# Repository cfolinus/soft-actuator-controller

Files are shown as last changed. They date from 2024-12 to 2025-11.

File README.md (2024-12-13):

# soft-actuator-controller
The Trajectory Cycle program serves as a means of running a cyclic actuator inflation test. 
This program is designed for the arduino nano platform and is intended to be used with a
2/2 NC solenoid valves arranged in a fill/bleed circuit. The program is designed to be used with any soft pneumatic actuator, and requires tuning of PID gain values for different actuators. Zeigler-Nichols method is a recommended starting point.

The codebase will not be able to properly upload to the controller unless it is correctly formatted for your computer. Be sure to follow the PlatformIO and codebase installation instructions found in the "Install, Tune, & Run the Controller" How-to guide.

In the codebase, the main control loop can be found in main.cpp, but all variables relevant to the adjustment of the controller can be found in adjustableSettings.cpp. For details on how the controller works, what purpose it serves, what all relevant variables do, and how to tune the controller, please refer to the Powerpoint presentation and word documents included in this directory.

--Evan Comiskey, 2024/08, MIT Fabrication-Integrated Design Lab, comiskey@mit.edu

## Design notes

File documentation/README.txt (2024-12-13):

The Trajectory Cycle program serves as a means of running a cyclic actuator inflation test. 
This program is designed for the arduino nano platform and is intended to be used with a
2-way proportional solenoid valves arranged in a fill/bleed circuit. The program is designed to be used with any soft pneumatic actuator, and requires tuning of PID gain values for different actuators. Zeigler-Nichols method is a recommended starting point.

The codebase will not be able to properly upload to the controller unless it is correctly formatted for your computer. Be sure to follow the PlatformIO and codebase installation instructions found in the "Install, Tune, & Run the Controller" How-to Word document in the documentation sub-folder before downloading the entire GitHub repository.

In the codebase, the main control loop can be found in main.cpp, but all variables relevant to the adjustment of the controller can be found in adjustableSettings.cpp. For details on how the controller works, what purpose it serves, what all relevant variables do, and how to tune the controller, please refer to the Powerpoint presentation and word documents included in the documentation directory.

--Evan Comiskey, 2024/12, MIT Fabrication-Integrated Design Lab, comiskey@mit.edu

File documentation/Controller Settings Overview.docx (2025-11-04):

# Pneumatic Actuator Test Stand

# Controller Settings Overview

Evan Comiskey – MIT FID Lab – 2024/08 – comiskey@mit.edu

# Description:

This guide walks you through the functions of all variables relevant to the operation and adjustment of the test stand’s PID control software, in the order in which they appear in the main settings file. Any implied or uncontextualized purposes of variables discussed in this overview can likely be explained by reviewing the Test Stand & Controller Overview PowerPoint document

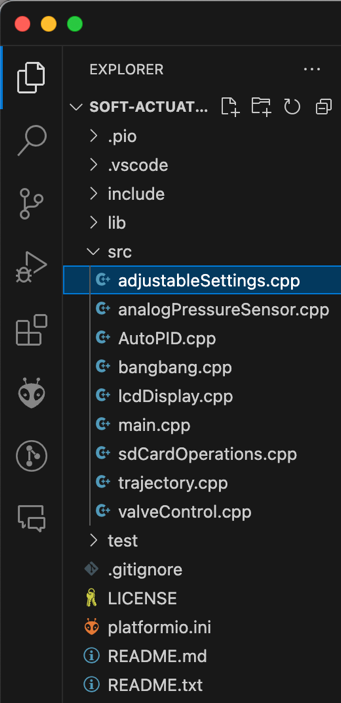
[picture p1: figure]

# 1. Where Relevant Settings Live

- You only need to interact with adjustableSettings.cpp to use the controller as originally designed in August 2024.
  - It is located within the src sub folder of the downloadable codebase shown at right.
  - For information on how to set up the codebase, see the Install, Tune, & Run the Controller Word document.

# 2. Pin Definitions

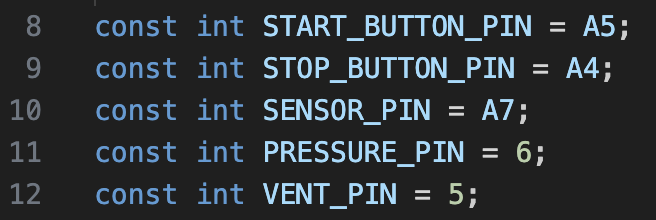
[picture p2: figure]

- The first five variables are static pin definitions for all the valves, sensors, and buttons involved in the controller logic. They should never be changed once initially set, unless the arrangement of your physical electronics has changes too.
  - Change the default definitions listed to those appropriate to your set-up if they differ.
  - PRESSURE_PIN and VENT_PIN must be PWM-capable pins on your microcontroller; if they aren’t the controller won’t be able to open/close the solenoid valves.

# 3. Pneumatic Valve Settings

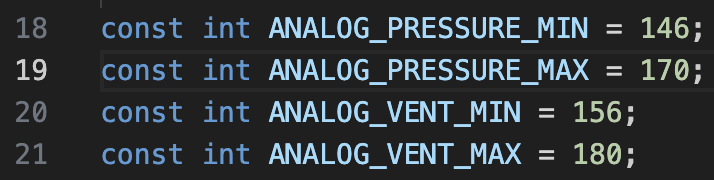
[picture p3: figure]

- These four variables dictate the minimum and maximum analog signals that can be sent to the solenoid valves.
  - The defaults listed in the code are specific to the set-up originally created for the MIT Fabrication-Integrated Design Lab in August 2024. Anytime you create a new version of this set-up with a different solenoid valve, even with the same exact model as listed in the original BOM, you must tune the controller program for that specific 2/2 solenoid valve.
  - Due to mechanical wear in the valves, you may need to retune your solenoid valves if you notice consistent, unexpected poor controller behavior.
- Tune the solenoid valve by following the tuning procedure described in the Install, Tune, & Run the Controller file.

# 4. Filename Setting

- The fileName setting allows the use of custom naming schemes for the test files generated by the controller. There is no restriciton on what can be included in the name, so long as it totals less than 50 characters.
- Test files are generated in the form fileName_#.csv, where # represents the lowest unused integer whereever the file is being saved.
  - At the start of a test, If cycle_test_1, and cycle_test_2 already exist, the controller will automatically create a new cycle_test_3 file to store the new test’s data

# 5. Tuning Settings

- TUNE_PRESSURE and TUNE_VENT should always be set to false, unless the system’s pressure and vent valves are being tuned as outlined in section 5 of the Install, Tune, & Run the Controller guide.

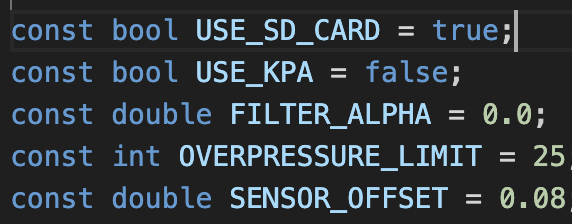
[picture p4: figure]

# 6. Pressure Sensor Settings

- USE_SD_CARD dictates where the data the controller generates during a test is sent.
  - If set to true, the controller writes all test data to a new csv file on the SD card.
  - If false, writes all test data to the serial port, where it can be intercepted and plotted in real-time by the LiveSerialPlotting.m script.
    - This will save all data to excel files of the form fileName_MATLAB_#.csv
    - Allows for quicker gain-tuning workflows
- The second of the five pressure-related settings is the USE_KPA Boolean.
  - If set to true, will interpret all pressure related values and variables in Kilopascals.
  - All pressure data coming from the pressure sensor will automatically be interpreted in units of Kpa and will be written to the microSD card that way as well.
  - If USE_KPA is set to false, the system behavior will remain the same, but use units of PSI.
- FILTER_ALPHA is passed to the pressure sensor collection logic and implemented as the coefficient in a simple low pass filter used to smooth the pressure data which is eventually fed to both the PID controller and recorded to the SD Card. \
  - During preliminary testing, it was found that even a filter alpha as low as 0.01 would make the controller noticeably more unstable for negligible smoothing benefit.
  - It is typically best to leave the controller off by setting the alpha equal to 0.
- OVERPRESSURE_LIMIT serves as a safety measure to prevent accidental overinflation of actuators.
  - Set the variables just under the safe operating limit of your actuator.
    - If your actuator bursts at 30 PSI, you will likely want to set this value somewhere around 25 PSI.
  - This setting directly interferes with burst testing trajectories and can lead to premature test endings, so be sure to alter along with your trajectory as appropriate.
  - It is not recommended to manually set a pressure max by adjusting the regulator down, as a lower inlet pressure differential will lead to a worsened ability for the controller to follow its programmed trajectory.
- SENSOR_OFFSET exists to allow calibration of the pressure sensor used in the system. Once set for a specific pressure sensor
  - It will not need to be adjusted again.
  - The offset will be different for every sensor
  - Recommend finding the offset for a specific pressure sensor using simple Arduino code that prints pressure values to Serial while the sensor sits at normal atmospheric conditions.

# 7. Frequency Settings

- These three settings determine the rate at which the microcontroller performs the following tasks:
  - Reads and writes the pressure data.
  - Writes other controller and cycle-related variables to the microSD card.
  - Performs trajectory interpolation (refer to the trajectory section for more information).
  - Updates the output of the PID controller.
- These values are frequency settings, but they must be set in units of milliseconds.
- It is recommended to keep these variables at their default values based on initial performance testing.
- If you do change these values, it is recommended to:
  - Keep INTERP_CALC_DELAY and CONTROLLER_DELAY at the same value. Performance seems to improve when both actions occur in sync.

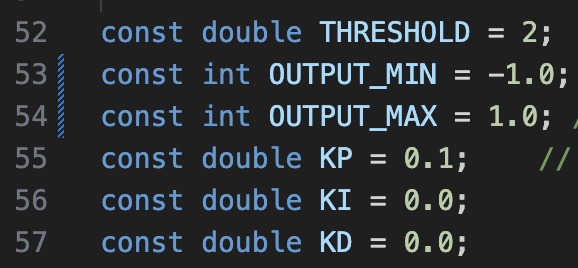
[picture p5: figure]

# 8. PID Controller Settings

- These 6 variables relate to the overall behavior of the proportional-integral-derivative (PID) controller and its outputs.
- THRESHOLD represents the range outside of which a test will fail if the controller fails to follow a non-zero setpoint.
  - If you set your trajectory function as a 15 PSI step function and set a 2 PSI threshold, then the test stopping safety logic will activate if the controller fails to stay within a range of 13-17 PSI for more than 2 seconds.
  - The added time delay prevents disturbances from abruptly ending tests early. It is recommended to set this threshold to 50% of your operating pressure for long form cycle or burst testing, to be able to characterize actuator behavior after material failure.
- OUTPUT_MIN and OUTPUT_MAX are helper variables that are used to map the outputs of the PID controller to the PWM signals defined in section 3 of this guide.
  - Do not change these variables from their defaults if you are not doing major restructuring to the code’s logic.
- KP, KI, and KD represent the gains for the proportional, integral, and derivative controller actions respectively.
  - Preliminary testing suggests starting with a KP value on the order of 10⁻¹, and a KI value on the order of 10⁻³
  - Do not involve derivative control (i.e., keep KD at 0) given its tendency to introduce high frequency instability into PneuNet systems.

# 9. Trajectory Settings

- The last two variables listed in the file concern defining the trajectory settings of your controller.
  - For more definition on how to develop a trajectory function for the actuator to follow, see the Write Custom Trajectory Functions word document.
- TIMES is an array of time setpoints expressed in milliseconds, and PRESSURES contains the associated pressure setpoints for each time instance.
  - Ensure that these arrays are of the same length, else the program will fail to run properly.
- For convenience, example Step, Sawtooth, Reverse Sawtooth, Triangle, Sine, Ramp, and Burst trajectories have been included in the file as starting points for the development of your own custom trajectories.
  - Because these variables are defined as constant (const) in the program, only one set of definitions for TIMES and PRESSURES can be uncommented at once, else the code will fail to compile.

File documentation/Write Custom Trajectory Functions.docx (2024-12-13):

# Pneumatic Actuator Test Stand

# Writing Custom Trajectory Functions

Evan Comiskey – MIT FID Lab – 2024/08 – comiskey@mit.edu

# Description:

This guide will walk you through the details and intricacies of the trajectory functions used by this controller, which define the pressure profile the controller attempts to follow through each cycle of the controller

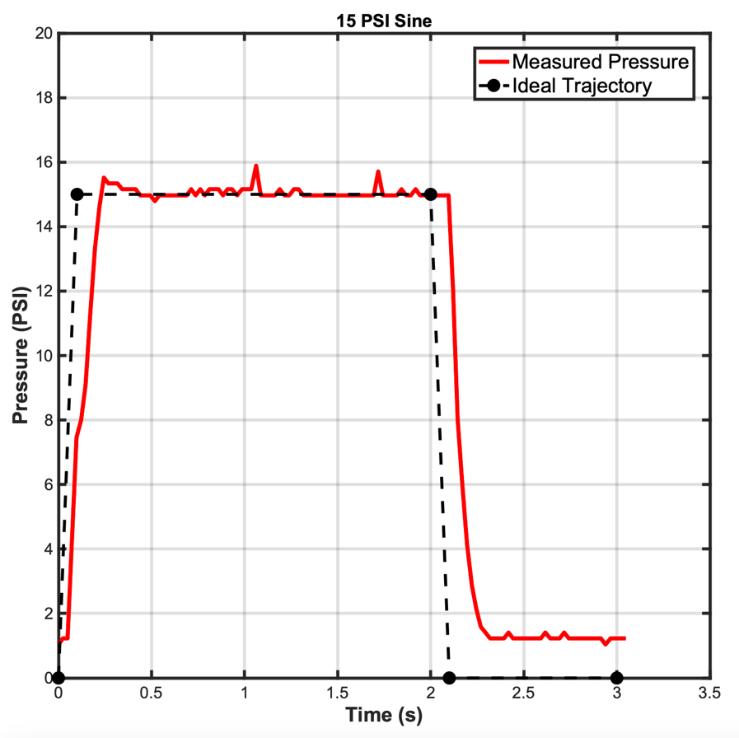
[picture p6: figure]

# 1. What is a Trajectory Function?

- A trajectory function, as defined for this controller logic, is a pressure profile that is defined by the user, and instructs the controller what pressure the system should be targetting at any given point in time.
  - The user defines this function by filling TIMES and PRESSURES, two arrays of equal sizes, in the adjustableSettings.cpp file.
  - Both variables are passed to the Trajectory object in main.cpp to be used in tandem with the autoPID controller object.
    - The times are to be listed in milliseconds, and the pressures will be interpreted either in Kpa or PSI values, depending on whether or not the USE_KPA boolean is set to true or false respectively.
- Testing thus far has shown no negative impact to controller behavior when defining the trajectory function instantaneous setpoints
  - I.e., testing indicates TIMES = [0, 0, 2000, 2000, 3000] and PRESSURES = [0, 15, 15, 0, 0] should produce a response very similar to the one shown above
- These trajectory functions can be very simple, or very complex, depending on the shape of the curve one wishes their pressure profile to follow.
  - The simpler the curve—such as the step function shown above—the less points one needs to use to define it.
- Once the last pair of a trajectory’s setpoints is reached, the controller automatically loops back to the beginning of the cycle function. This allows for long form cycle testing.
  - Long form cycle testing can be used to characterize an actuator’s behavior over its usable lifetime as its material components wear with extended use.
- The Trajectory class’s interp() function allows the controller to know what to set the pressure to in between defined points.
  - Interp() takes in a variable deltaT, which is the time since the start of the current cycle and compares it against the values in the TIMES array.
  - The interp() function determines which two coordinates deltaT is between, and linearly interpolates a corresponding pressure value for that time value from the PRESSURES array.
  - The linear interpolation equation used is as shown:

P_(interpolated) = P_1 +((∆T-t_1)/(t_2 -t_2))×(p_2 -p_1 )

- Structuring the trajectories this way has several benefits:
  - Long hold times at a constant pressure can be written as simply two-time setpoints with equal pressure values
  - allows for quick modification, iteration, and development of different or evolving trajectory profiles as relevant to your task.

# 2. Writing Custom Trajectory Functions

- You will more than likely want to write your own trajectory functions different than the ones included in the controller.
- Several example structures for various control signal shapes such as step, triangle, sawtooth, and sine waves are included by default in adjustableSettings.cpp and can be uncommented and adjusted to fit your needs.
  - Please see the Test Stand & Controller Overview PowerPoint for visualizations of these example signals at varying pressure magnitudes.
  - You do not have to only follow these curves or signal styles in the development of your own. They are meant to serve as handy starting points and building points.
- The possible trajectories one could make for this controller are virtually limitless, unconstructed by time.
  - The only limitations in trajectory creation are the limits of your hardware, and the memory size of the microcontroller.
  - The code has been structured such that there is ample memory space available in the program to develop highly complex setpoints beyond what is showcased by the documentation.
- The only major caveat to the creation of trajectory functions is how you begin and end them. Unless you plan to stop the test before one full cycle completes, the cyclic nature of the controller means that the moment the trajectory ends, the controller begins interpolating between the first and second setpoint of the trajectory during the next cycle immediately. As such, for smooth cycling, it is recommended that you set the first and last setpoints of your PRESSURES array equal.
  - It is further recommended that you set the first and last pressure values to 0. While the controller is certainly capable of handling transitioning between the end of a cycle and the start of the next with non-zero setpoints, this will likely result in some controller instability during the first few cycles, depending on the time-length of your trajectory function.

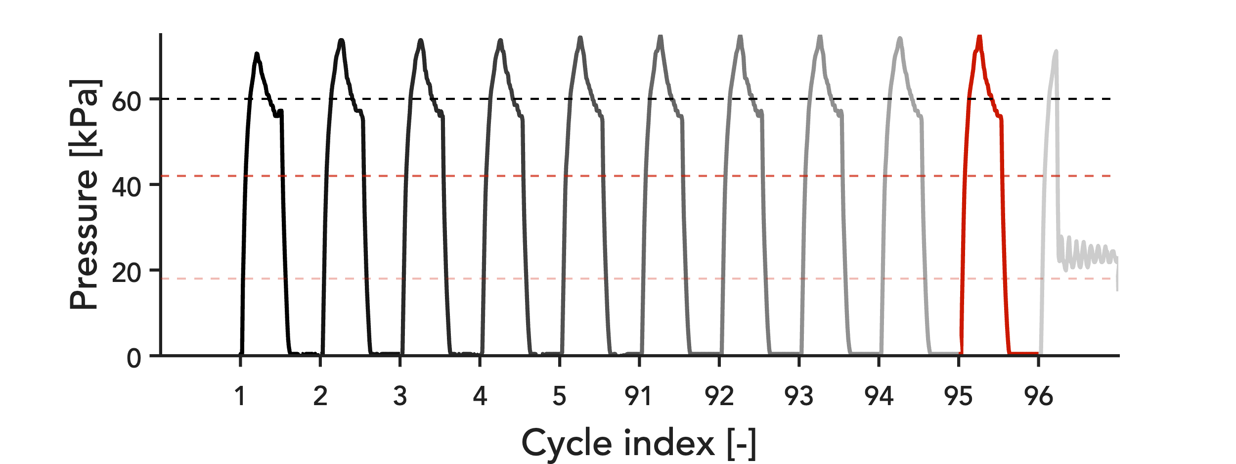
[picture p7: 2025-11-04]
data processing/figures/Harness/cycle_specimen14_trial2/Pressure cycles.png

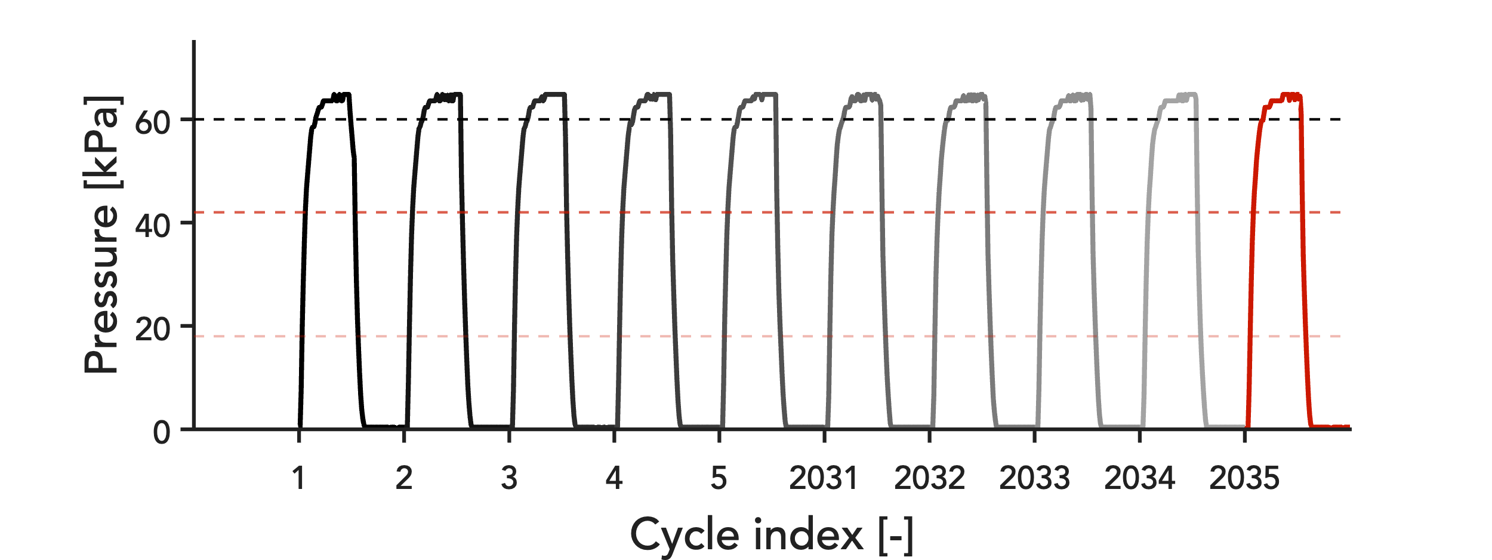
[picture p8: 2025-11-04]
data processing/figures/Harness/cycle_specimen26_trial5/Pressure cycles.png

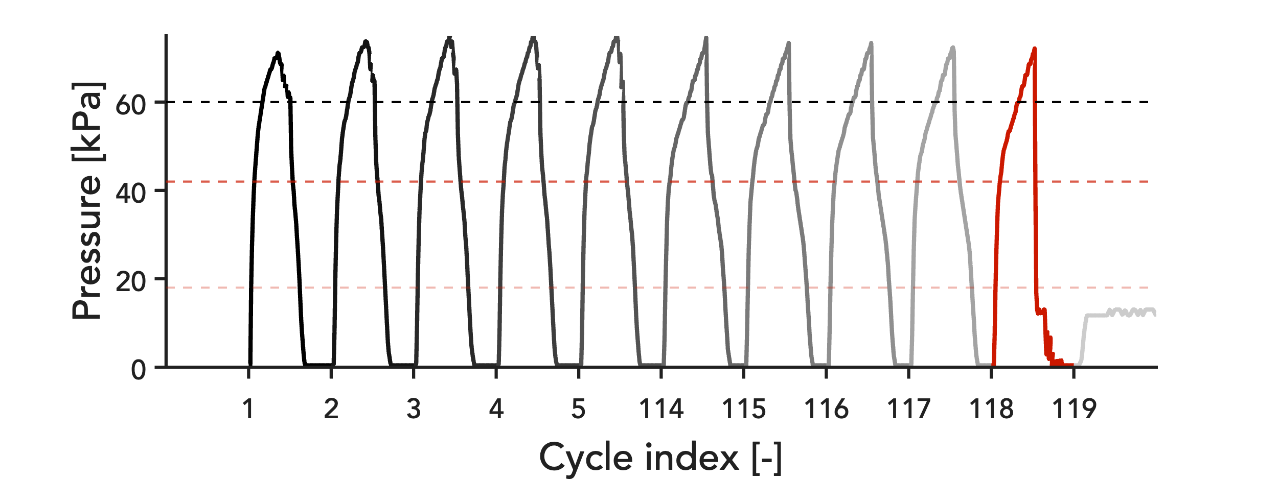
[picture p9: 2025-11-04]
data processing/figures/Bare/cycle_specimen53_trial1/Pressure cycles.png

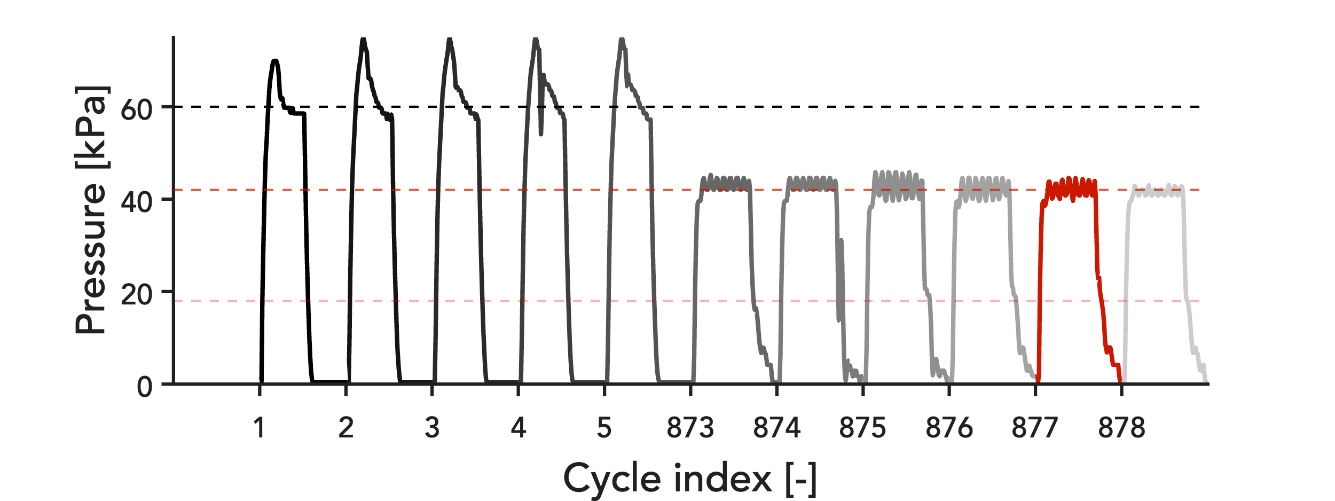
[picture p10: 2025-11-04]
data processing/figures/Green/cycle_specimen36_trial1/Pressure cycles.png

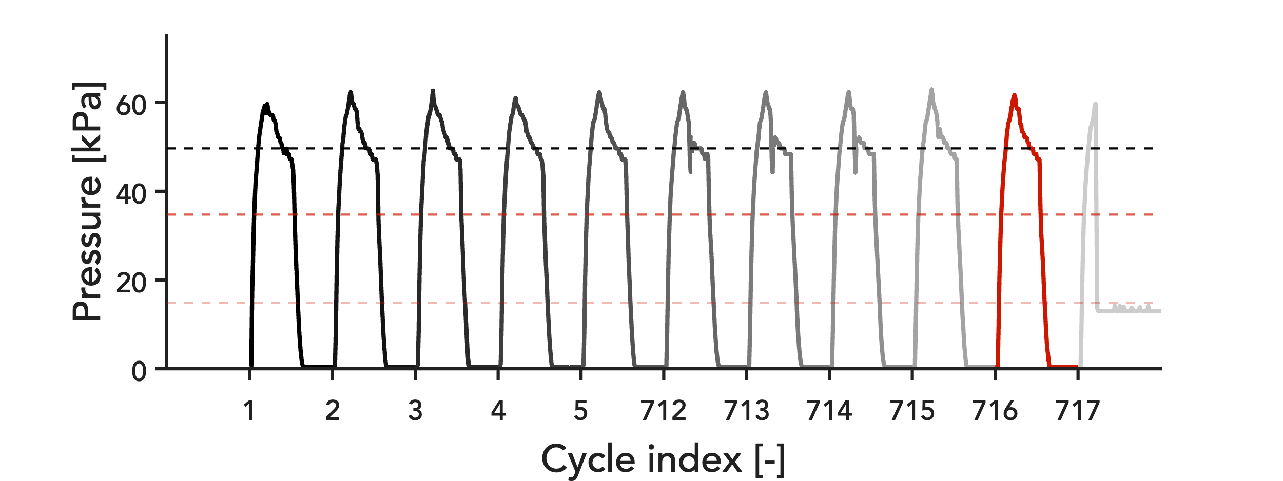
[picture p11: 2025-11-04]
data processing/figures/Harness/cycle_specimen12_trial3/Pressure cycles.png

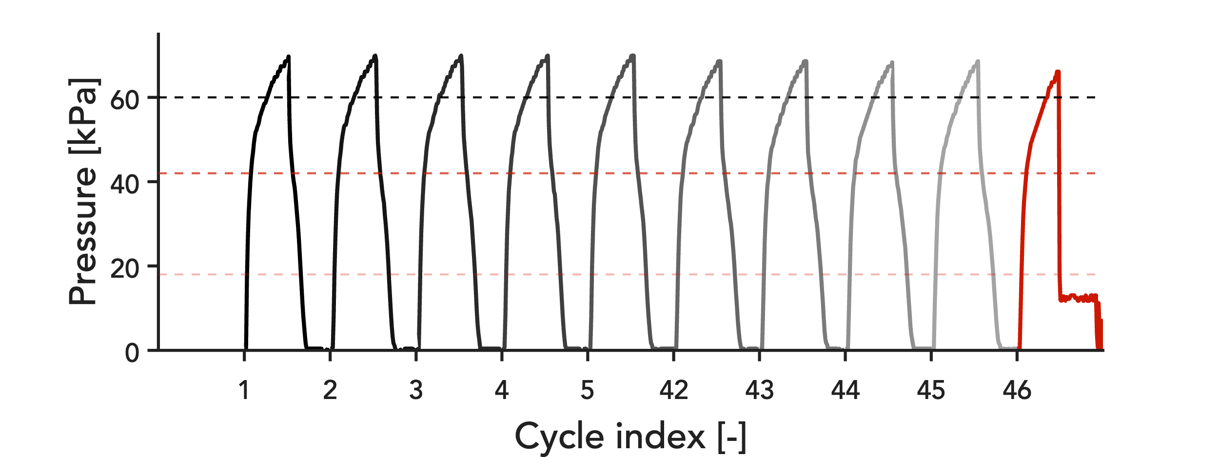
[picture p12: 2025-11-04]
data processing/figures/Bare/cycle_specimen16_trial2/Pressure cycles.png

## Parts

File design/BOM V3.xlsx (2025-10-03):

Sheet: TO ORDER
Category | Part type | Quantity | Quantity to order | Supplier | Part number | Leadtime | Notes | Cost per unit, approximate [$] | Total cost [$] | Part status
Hardware | End Cap, 20 mm profile | 8 | 8 | McMaster | 5537T14 | Ships immediately | A nice to have for finish. Not necessarily required | 1.2 | 9.60
Electronics | 24 Pack of Momentary Switch Buttons | Pkg | 1 | Amazon | https://www.amazon.com/Momentary-Button-Switch-Assorted-Self-Resetting/dp/B08SKJ6V7Z?cv_ct_cx=momentary+push+button+switch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 | Ships immediately |  | 11.49 | 11.49
Hardware | Standoffs, M3x0.5, 15mm | 8 | 8 | McMaster | 95947A511 | Ships immediately | Buck Converter & LCD Screen Mounting Standoffs | 1.47 | 11.76
Hardware | Standoffs, M5x0.8, 50mm | 6 | 6 | McMaster | 95947A565 | Ships immediately | Second Platform Mounting Standoffs | 1.99 | 11.94
Hardware | Bumper, M6x1, 18mm | 4 | 4 | McMaster | 3810N126 | Ships immediately | Platform Feet | 3.33 | 13.32
Hardware | Standoffs, M2x0.4, 6mm | 8 | 8 | McMaster | 93355A510 | Ships immediately | Solderboard standoff | 3.66 | 29.28
Hardware | Socket Head Screws, 6mm | Pkg | 1 | McMaster | 90128A178 | Ships immediately | Mounting Screws | 15.68 | 15.68

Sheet: Actuator Stand BOM
Category | Part type | Quantity | Quantity to order | Supplier | Part number | Leadtime | Notes | Cost per unit, approximate [$] | Total cost [$] | Order cost [$] | Part status
Hardware | End Cap, 20 mm profile | 8 |  | McMaster | 5537T14 | Ships immediately |  | 1.2 | 9.60 | 0.00 | Hold off for now - can add later
Hardware | Screw, M5x12mm | 32 |  | McMaster | 90128A236 | Ships immediately |  | 9.55 | 305.60 | 0.00 | Order placed
Hardware | Screw, M5x10mm | 36 |  | McMaster | 90128A234 | Ships immediately |  |  | 0.00 | 0.00 | Order placed
Hardware | Screw, M5x8mm (OPTIONAL) | 4 |  | McMaster | 90128A232 | Ships immediately | For optical table mounting |  | 0.00 | 0.00 | Order placed
Hardware | Nut, M5 | 16 |  | McMaster | 90591A260 | Ships immediately |  | 0 | 0.00 | 0.00 | Have in lab
Hardware | T-Nut, M5 | 52 |  | McMaster | 5537T651 | Ships immediately |  | 0 | 0.00 | 0.00 | Have in lab
Hardware | Screw, M6x8mm (OPTIONAL) | 4 |  | N/A (have in lab) | N/A | Have in lab | For optical table mounting | 0 | 0.00 | 0.00 | Have in lab
Hardware | T-slot, 20mm profile, 230mm long | 4 |  | Fabricated | CUSTOM | N/A | Vertical rails | 0 | 0.00 | 0.00 | To be machined
Hardware | T-slot, 20mm profile, 160mm long | 2 |  | Fabricated | CUSTOM | N/A | Top lengthwise rails
Hardware | T-slot, 20mm profile, 200mm long | 2 |  | Fabricated | CUSTOM | N/A | Bottom lengthwise rails
Hardware | T-slot, 20mm profile, 80mm long | 4 |  | Fabricated | CUSTOM | N/A | Width rails | 0 | 0.00 | 0.00 | To be machined
Hardware | Front Viewing Panel, 5mm Clear Acrylic | 1 |  | N/A (to fabricate) | CUSTOM | N/A | If swap to 3mm panels, knock M5x10mm down to M5x8mm | 0 | 0.00 | 0.00 | To be machined
Hardware | Right Viewing Panel, 5mm Clear Acrylic | 1 |  | N/A (to fabricate) | CUSTOM | N/A |  | 0 | 0.00 | 0.00 | To be machined
Hardware | Left Mounting panel, 5mm White Acrylic | 1 |  | N/A (to fabricate) | CUSTOM | N/A |  | 0 | 0.00 | 0.00 | To be machined
Hardware | Back Electronics panel, 5mm White Acrylic | 1 |  | N/A (to fabricate) | CUSTOM | N/A |  | 0 | 0.00 | 0.00 | To be machined
Hardware | Top Mounting panel, 5mm White Acrylic | 1 |  | N/A (to fabricate) | CUSTOM | N/A |  | 0 | 0.00 | 0.00 | To be machined
Hardware | elbow bracket, M5-to-M6 (OPTIONAL) | 4 |  | Printed | CUSTOM | N/A | For optical table mounting | 0 | 0.00 | 0.00 | To be machined
Hardware | gusset, M5 | 8 |  | N/A (to print) | CUSTOM | N/A |  | 0 | 0.00 | 0.00 | To be machined
Hardware | LCD Mount | 1 |  | N/A (to print) | CUSTOM | N/A |  | 0 | 0.00 | 0.00 | To be machined
Hardware | Start/Stop Button Mount | 1 |  | N/A (to print) | CUSTOM | N/A |  | 0 | 0.00 | 0.00 | To be machined

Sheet: ElectroPneumatics Box BOM
Category | Part type | Quantity | Quantity to order | Supplier | Part number | Leadtime | Notes | Cost per unit, approximate [$] | Total cost [$] | Order cost [$] | Part status
Electronics | SD card reader | 1 |  | Digikey | A135 | Ships immediately | Need 1x microcontroller Any SD card reader will do |  | 0.00 | 0.00 | Have in lab
Electronics | Toggle switch | 1 |  | Amazon | https://a.co/d/0gOuDZar | Ships immediately | Any will do that can take ≥24V | 6.5 | 6.50 | 0.00 | Order placed
Electronics | Flyback diode: need 1A with at least 24V safety | 4 |  | Digikey | 1N4001DICT-ND | Ships immediately | Need 2x per solenoid | 0.17 | 0.68 | 0.00 | Order placed
Electronics | Button, Green | 2 |  | Digikey | D6R50 F2 LFS | Ships immediately | Start Button, HOW TO MOUNT? |  | 0.00
Electronics | Button, Red | 2 |  | Digikey | D6R40 F2 LFS | Ships immediately | Stop Button |  | 0.00
Electronics | Pressure sensor: need 50(?) psi on 5V | 1 |  | Digikey | 480-6637-ND | Ships immediately | Accepts 0.19" male barb | 31.15 | 31.15 | 0.00 | Hold off for now - have 2 in lab
Electronics | MOSFETs, N-type | 2 |  | Digikey | IRLB8721PBF | Ships immediately | Need 1x solenoid, or 2x channel | 0.9 | 1.80 | 0.00 | Order placed
Electronics | Arduino Nano | 1 |  | Digikey | 1050-ABX00080-ND | Ships immediately | May replace in future versions | 20 | 20.00 | 0.00 | Order placed
Electronics | Resistors |  |  | N/A | N/A | Have in lab | Have in lab | 0 | 0.00 | 0.00 | Have in lab
Electronics | AC-DC Converter: 24V, Barrel Jack | 1 |  | N/A | N/A | N/A | Have in lab | 0 | 0.00 | 0.00 | Have in lab
Electronics | Breadboard/Solderboard | 1 |  | N/A | N/A | N/A | Have in lab | 0 | 0.00 | 0.00 | Have in lab
Electronics | Male Barrel Jack | 1 |  |  |  |  | For Plug in |  | 0.00 | 0.00 | Have in lab
Electronics | Female Barrel Jack | 1 |  |  |  |  | To go in Electrical housing on stand |  | 0.00 | 0.00 | Have in lab
Electronics | 16x2 I2C LCD Screen | 1 |  | Digikey | CN0295D | Ships immediately |  |  | 0.00
Electronics | Buck Converter, 24 V -> 7.5 V Capability | 1 |  | Digikey | DFR0379 | Ships immediately |  | 4.9 | 4.90
Electronics | Perfboard | 1 |  | Digikey | PRT-12070 | Ships immediately |  | 5.5 | 5.50
Pneumatics | Solenoids: 2-2 NC fill-bleed circuit | 1 |  | Clippard | EFB-1DV-24-L | Have in lab |  | 93.67 | 93.67 | 0.00 | Have in lab
Pneumatics | On/Off Valve | 1 |  | N/A (have in lab) |  |  | How to mount? |  | 0.00 | 0.00 | Have in lab
Pneumatics | Right-Angle Tee, for 1/4" Tube OD x 1/4" Stem OD | 1 |  | N/A (have in lab) | 5047K92 | Ships immediately | å | 1.56 | 1.56 | 0.00 | Have in lab
Pneumatics | Nylon Tubing, 1/4" OD, (Quantity in ft.) | 3 |  | N/A (have in lab) | N/A | Have in lab |  | 0 | 0.00 | 0.00 | Have in lab
Pneumatics | Regulator | 1 |  | N/A (have in lab) |  |  |  |  | 0.00 | 0.00 | Have in lab
Pneumatics | Pressure Gauge | 1 |  | N/A (have in lab) |  |  |  |  | 0.00 | 0.00 | Have in lab
Pneumatics | Plug Coupling, for 1/8" Barbed Tube ID, Nylon | 1 |  | McMaster | 51525K123 | Ships immediately |  | 0.49 | 0.49
Hardware | Standoffs, M3-0.5, 8mm | 4 | 4 | McMaster | 94868A164 | Ships immediately | Buck Converter Mounting | 1.26 | 5.04 | 5.04
Hardware | Standoffs, M5-0.8, 50mm | 6 | 6 | McMaster | 94868A767 | Ships immediately | Second Platform Mounting Standoffs | 3.45 | 20.70 | 20.70
Hardware | Bumper, M6-1, 18mm | 4 | 4 | McMaster | 3810N126 | Ships immediately | Platform Feet | 3.33 | 13.32 | 13.32

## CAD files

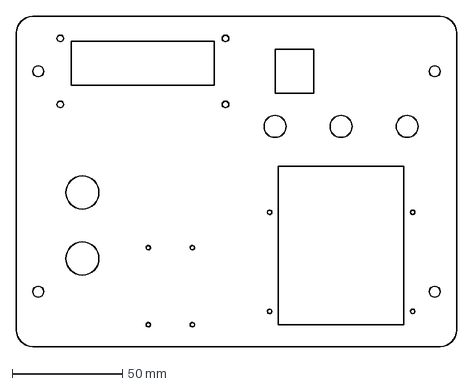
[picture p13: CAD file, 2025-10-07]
design/Electronics box/Electronics box (Entity_0).DXF
200.0 x 150.0 mm

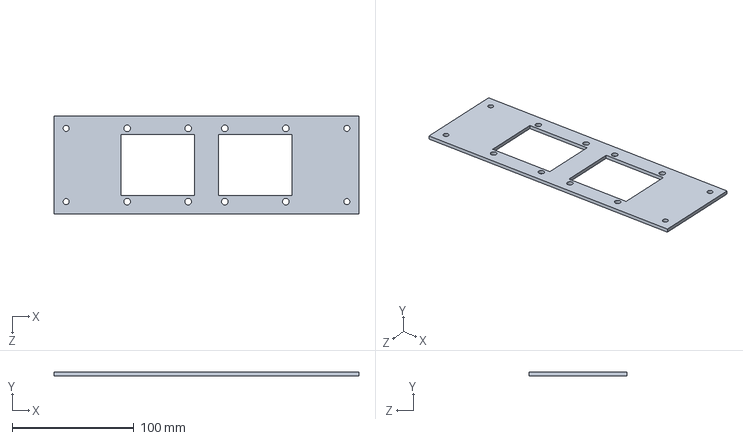
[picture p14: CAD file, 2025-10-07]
design/V3b/TopPlate.SLDPRT
250.0 x 3.00 x 80.0 mm

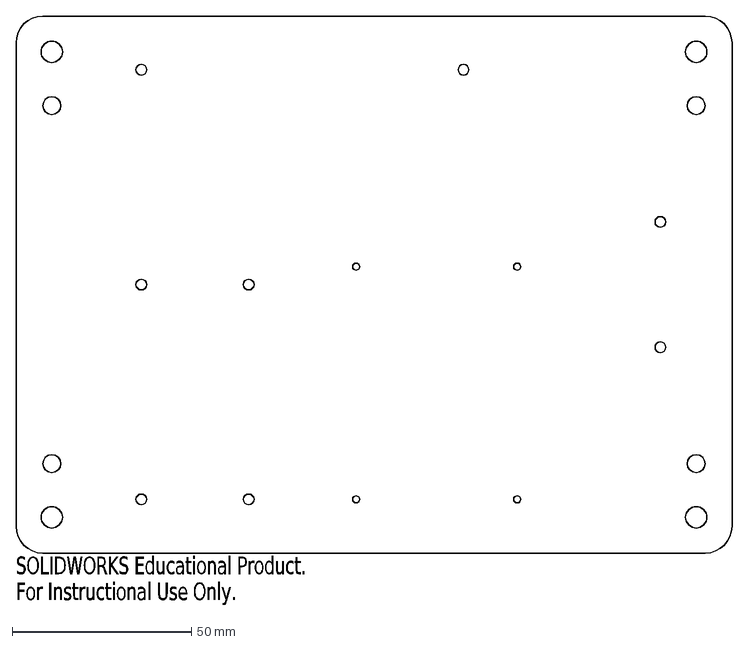
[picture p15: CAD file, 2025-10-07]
design/Electronics box/Electronics box (Entity_1).DXF
SOLIDWORKS Educational Product.
For Instructional Use Only.

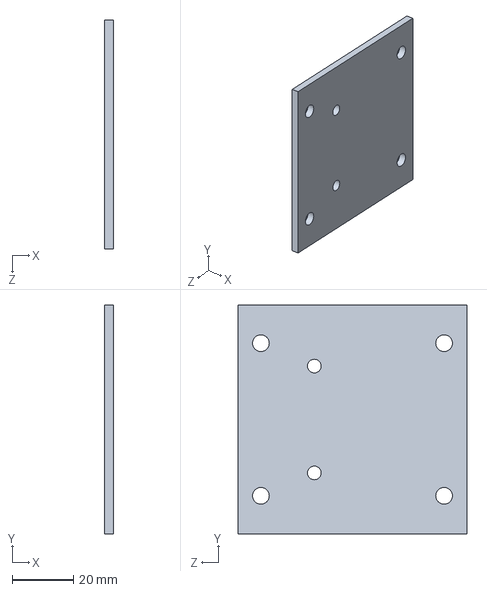
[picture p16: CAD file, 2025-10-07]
design/TestStand V3 CAD/ObjectMountPlate.SLDPRT
3.00 x 75.0 x 75.0 mm

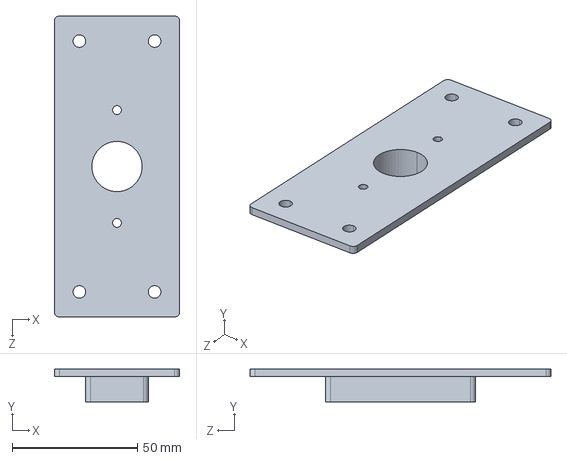
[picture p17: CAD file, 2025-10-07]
design/V3b/Actuator - Cat baseline.STEP
50.0 x 13.0 x 120.0 mm

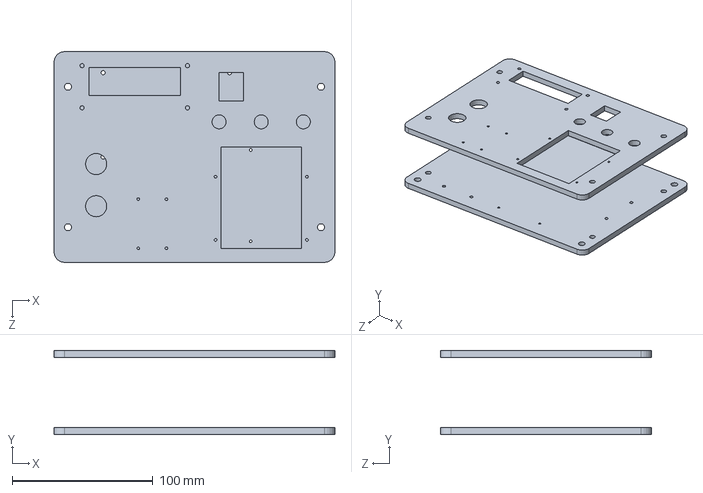
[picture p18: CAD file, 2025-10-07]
design/Electronics box/Electronics box.SLDPRT
200.0 x 60.0 x 150.0 mm

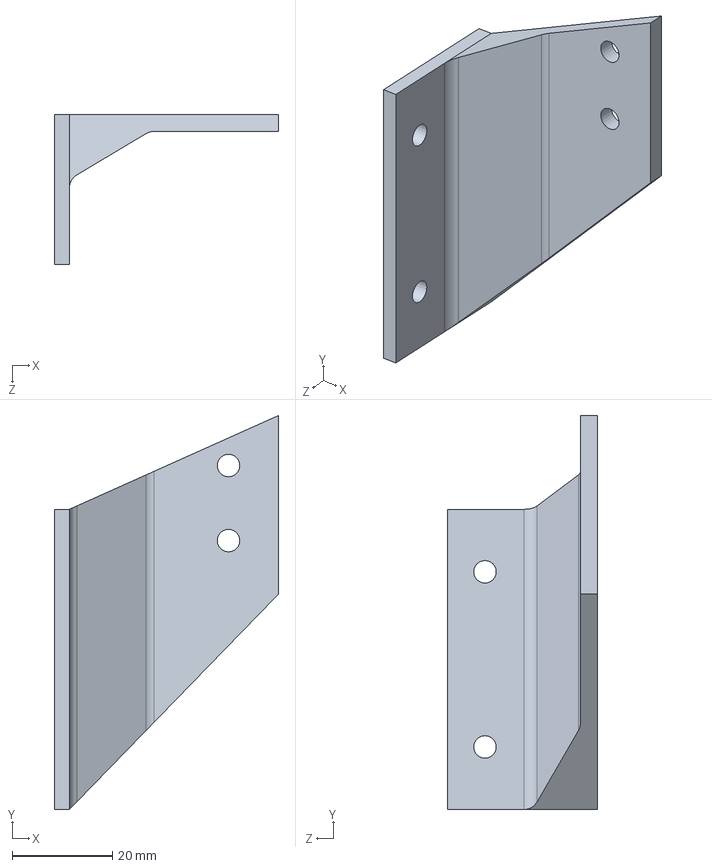
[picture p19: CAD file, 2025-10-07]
design/TestStand V3 CAD/ObjectMount.SLDPRT
44.8 x 78.7 x 30.0 mm

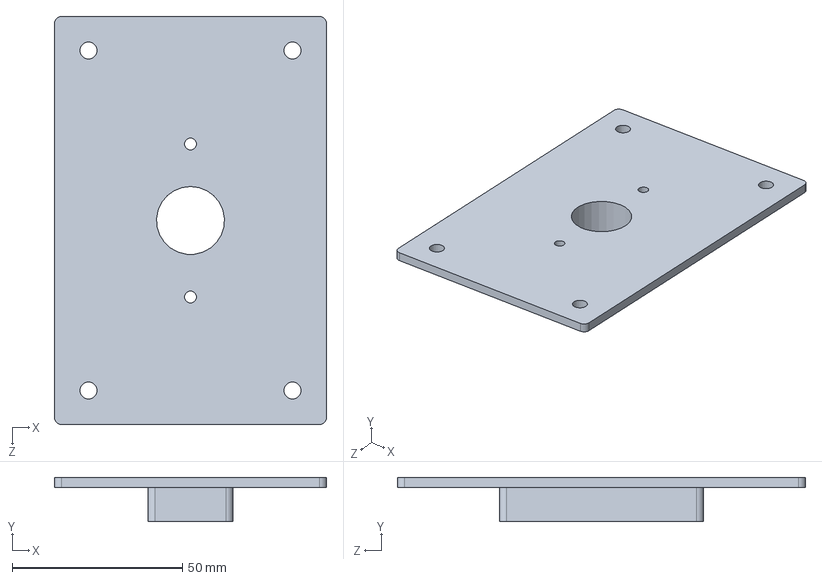
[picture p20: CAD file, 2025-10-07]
design/TestStand V3 CAD/TopPlate.SLDPRT
80.0 x 13.0 x 120.0 mm

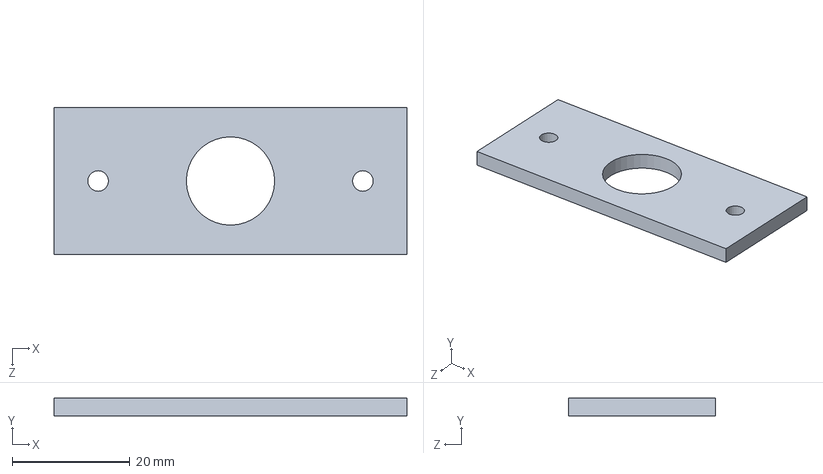
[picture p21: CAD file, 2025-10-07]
design/V3b/Actuator mount - Cat.SLDPRT
60.0 x 3.00 x 25.0 mm

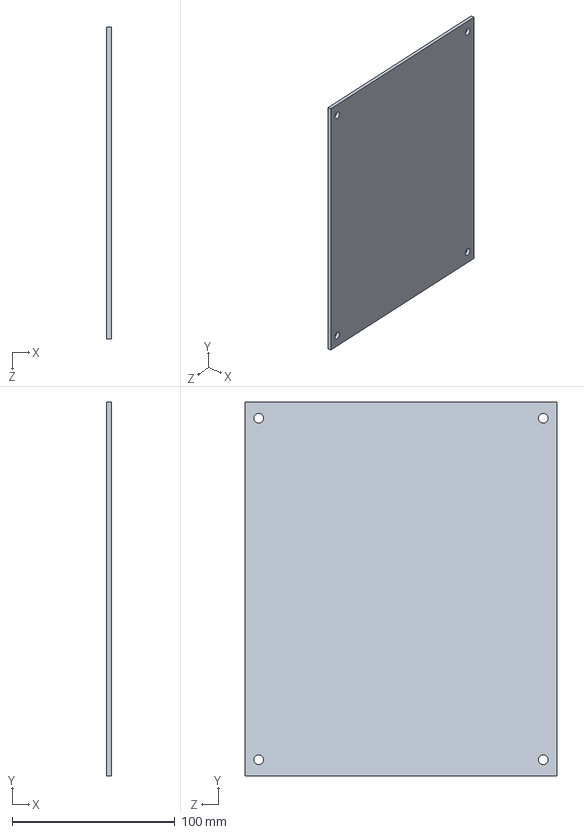
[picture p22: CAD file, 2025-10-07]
design/TestStand V3 CAD/RightPlate.SLDPRT
3.00 x 230.0 x 192.0 mm

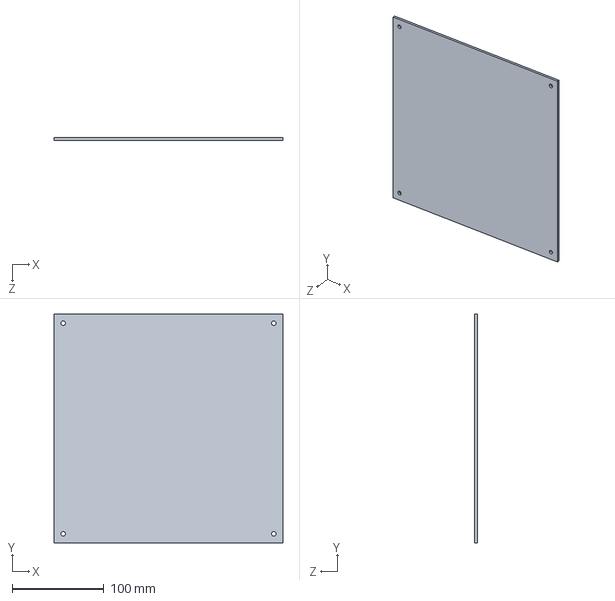
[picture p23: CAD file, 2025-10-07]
design/V3b/BackPlate.SLDPRT
250.0 x 250.0 x 3.00 mm

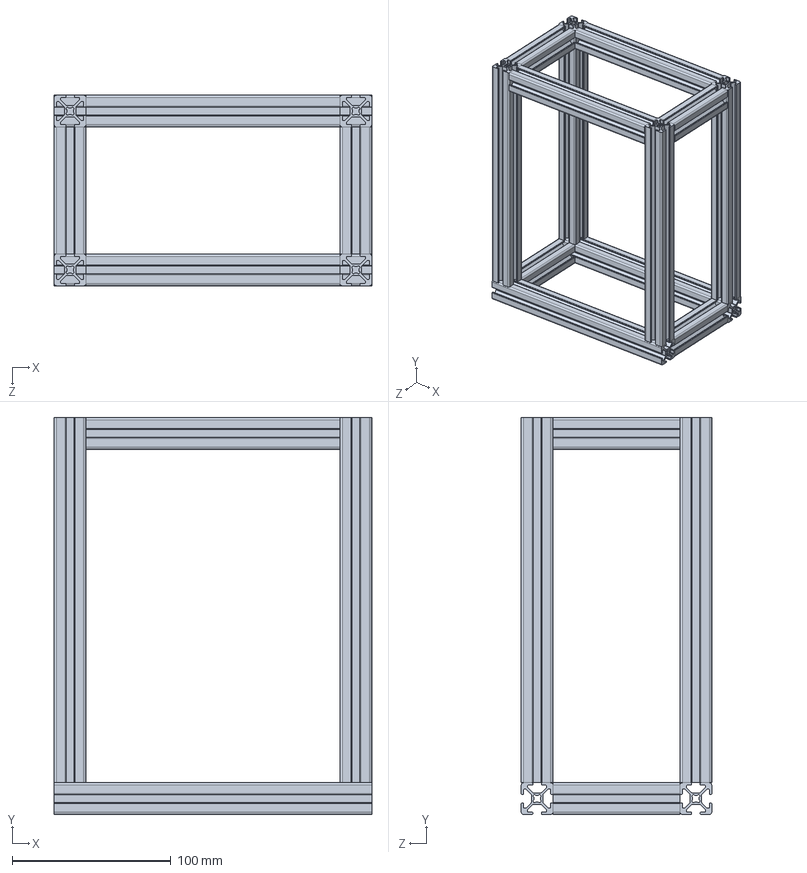
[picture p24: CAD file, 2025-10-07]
design/TestStand V3 CAD/TestStandFrame.SLDPRT
200.0 x 250.0 x 120.0 mm

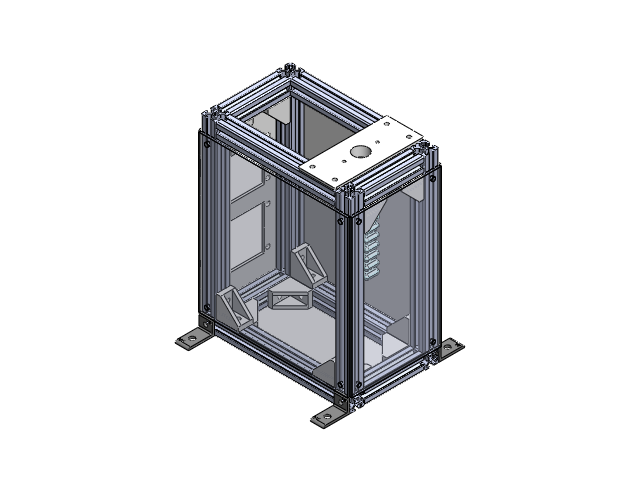
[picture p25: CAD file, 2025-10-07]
design/TestStand V3 CAD/TestStand.SLDASM
2020 rail - M5 corner bracket x 12
TestStandFrame
BackPlate
FrontPlate
LeftPlate
RightPlate
TopPlate
OpticalTableBracket x 4
Actuator mount - Cat
Actuator - Cat baseline

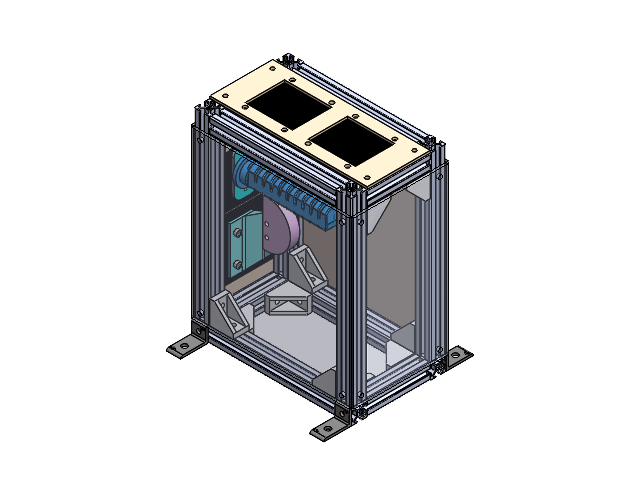
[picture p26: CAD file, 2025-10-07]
design/V3b/TestStand.SLDASM
2020 rail - M5 corner bracket x 12
TestStandFrame
BackPlate
FrontPlate
LeftPlate
RightPlate
TopPlate
OpticalTableBracket x 4
ActuatorPlate
91290A140_Alloy Steel Socket Head Screw x 2
CoverPlate x 2
ObjectMountPlate
ActuatorMount - 1-8NPT
Baseline - actuator
ObjectMount
ExampleObject - Disc

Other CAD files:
design/TestStand V3 CAD/ActuatorPlate.SLDPRT
design/V3b/ObjectMount.SLDPRT
design/TestStand V3 CAD/CoverPlate.SLDPRT
design/V3b/ObjectMountPlate.SLDPRT
design/TestStand V3 CAD/BackPlate.SLDPRT
design/TestStand V3 CAD/FrontPlate.SLDPRT
design/TestStand V3 CAD/LeftPlate.SLDPRT
design/V3b/2020 rail - M5 corner bracket.SLDPRT
design/V3b/91290A140_Alloy Steel Socket Head Screw.SLDPRT
design/V3b/Actuator - Cat baseline.SLDPRT
design/V3b/ActuatorMount - 1-8NPT.SLDPRT
design/V3b/ActuatorPlate.SLDPRT
design/V3b/Baseline - actuator.SLDPRT
design/V3b/Baseline - actuator.step
design/V3b/CoverPlate.SLDPRT
design/V3b/ExampleObject - Disc.SLDPRT
design/V3b/FrontPlate.SLDPRT
design/V3b/LeftPlate.SLDPRT
design/V3b/OpticalTableBracket.SLDPRT
design/V3b/RightPlate.SLDPRT
design/V3b/TestStandFrame.SLDPRT

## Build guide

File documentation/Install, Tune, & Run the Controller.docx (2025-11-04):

# Pneumatic Actuator Test Stand

# Install, Run, & Tune the Controller

Evan Comiskey – MIT FID Lab – 2024/08 – comiskey@mit.edu

# Description:

This How-To serves as a guide for installing the Pneumatic Actuator Test Stand’s PID control software. It will walk you through the entire process, from downloading an IDE to code, all the way to fine tuning your solenoid valve and associated controller gains. This guide assumes you have a functional hardware and electronics set-up, featuring an Arduino Nano board with PWM capabilities. Please reach out if you feel any critical information to be missing from this guide.

# 1. Installing PlatformIO

- Use an Interactive Development Environment (IDE) capable of running PlatformIO (https://platformio.org/) projects.
  - Skip to section 2 now if your IDE already supports PlatformIO projects.
- PlatformIO Overview:
  - PlatformIO is an open-source tool for working with embedded electronics systems like Arduino microcontrollers.
  - It offers a more in-depth and organized way to work with microcontroller code than the standard ArduinoIDE.
  - Can be run using various free and popular IDEs listed here. (https://platformio.org/install/integration)
- Setting up PlatformIO on Visual Studio Code (VS Code):
  - Download VS Code for Windows, Mac, or Linux at this link (https://code.visualstudio.com/download) or by going to https://code.visualstudio.com/download.
  - Follow all default installation instructions, as PlatformIO does not require you to do anything specific during VS Code’s installation.
- Once you have successfully installed VS Code, you will see a screen as shown:

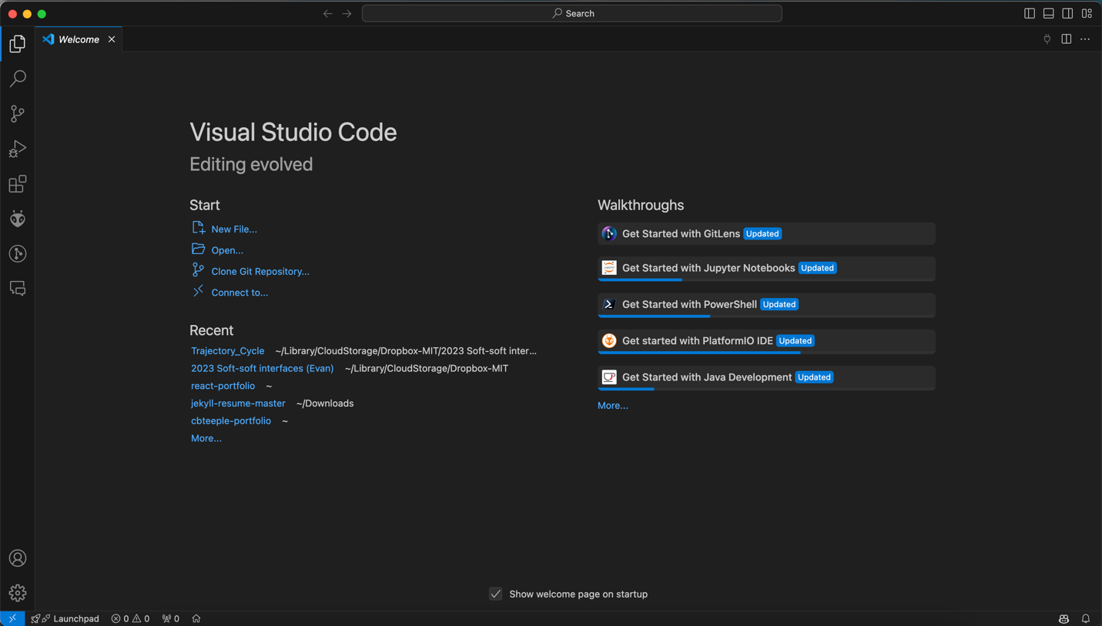
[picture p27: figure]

  - Feel free to go through VS Code’s provided tutorials as is necessary to familiarize yourself with the application.
- Install necessary C/C++ Dependencies
  - click the Extensions tab shown in the menu bar near the top left of the screen, highlighted in red below at left.
  - Type “C” into search bar. This will cause C/C++ by Microsoft to appear. This is the language which PlatformIO depends upon, so we must download it beforehand.

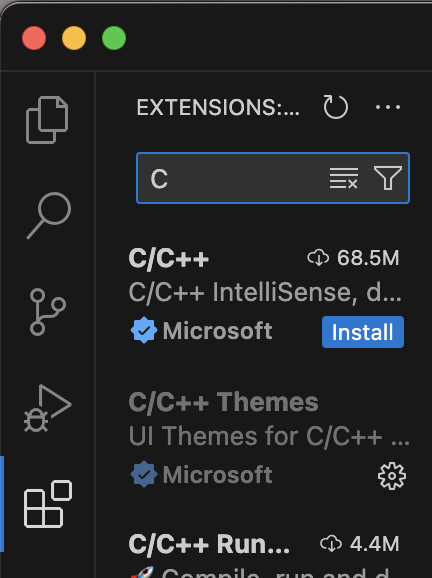
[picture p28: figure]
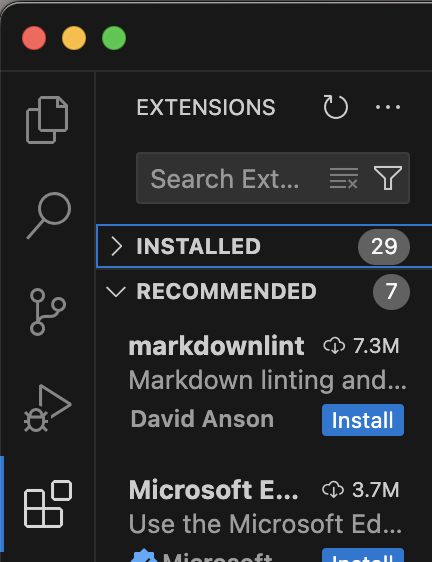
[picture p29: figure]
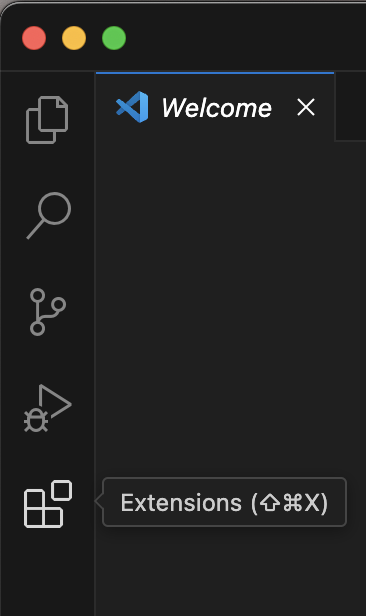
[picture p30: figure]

  - Click the install button for the extension.
- Similarly search for PlatformIO in the search bar. Download the first option that appears in the dropdown.
  - The author of this extension will also be named PlatformIO.
  - If you click on the extension, you should see a preview page which looks like the image shown at right.

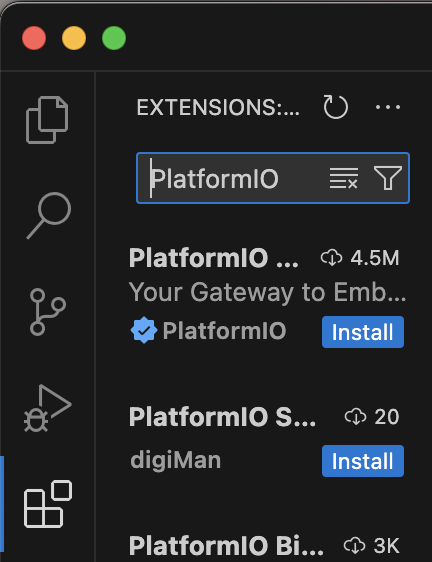
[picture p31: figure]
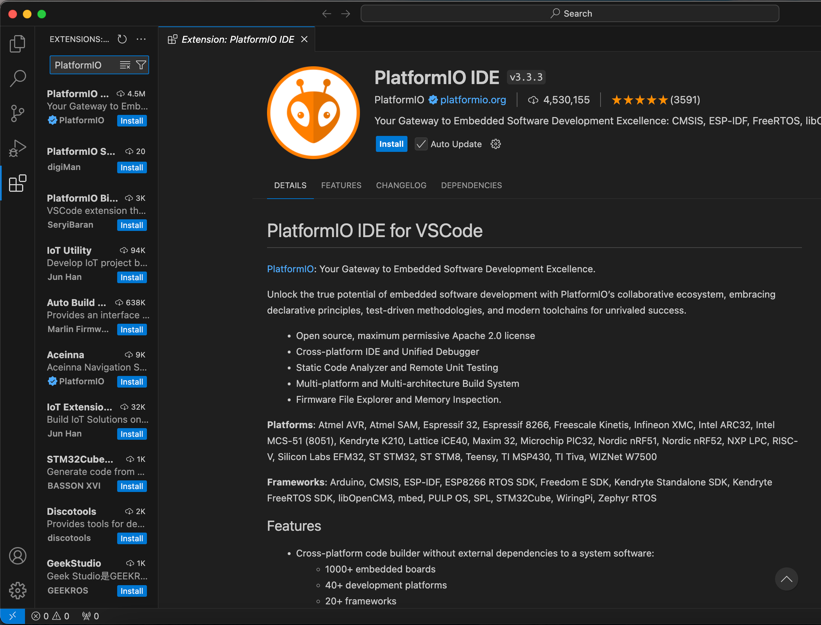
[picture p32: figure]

  - It will take a few minutes for PlatformIO to fully install. Once the application is fully installed, you will be prompted to quickly restart VS Code
- You will see a PlatformIO alien-head icon appear in the righthand menu where the extensions tab was once the application has successfully been installed.
  - Clicking on this icon will bring up the PlatformIO project tasks and quick access menus.
  - Press the PIO Home Open button in the quick access menus to bring up the PlatformIO homepage.
- You can start brand new projects from the PlatformIO homepage.

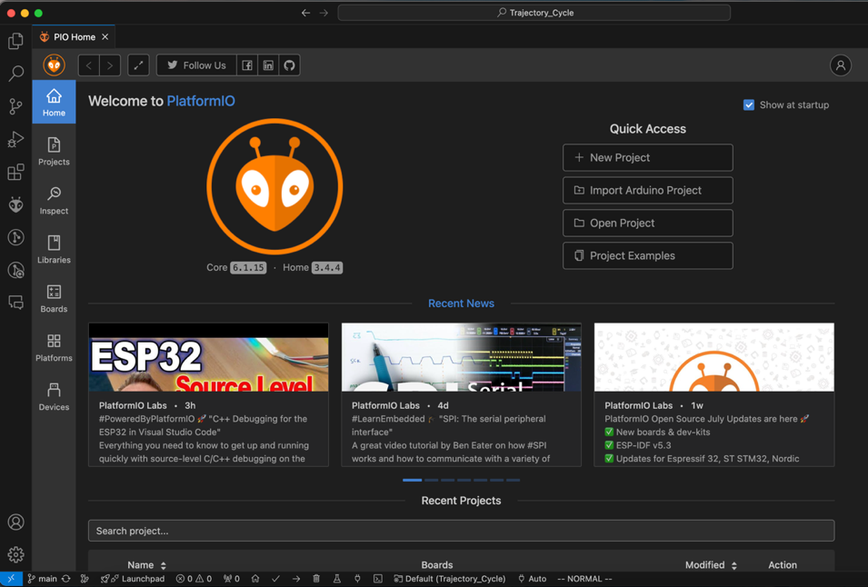
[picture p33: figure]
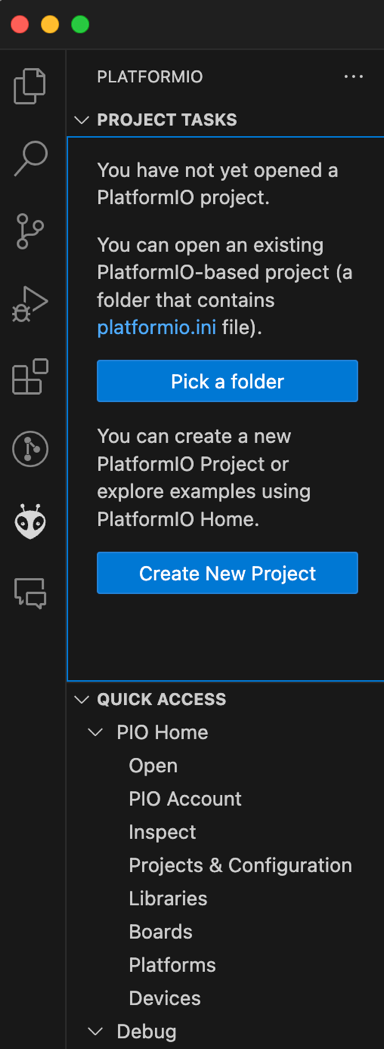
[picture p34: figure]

- PlatformIO is successfully installed if you see the home screen shown below at right, and you are ready to start working with this project’s codebase.

# 2. Downloading the Codebase

- Download the codebase by accessing the GitHub repository associated with this project by clicking here (https://github.com/Comiskey/soft-actuator-controller), or by going to https://github.com/Comiskey/soft-actuator-controller.

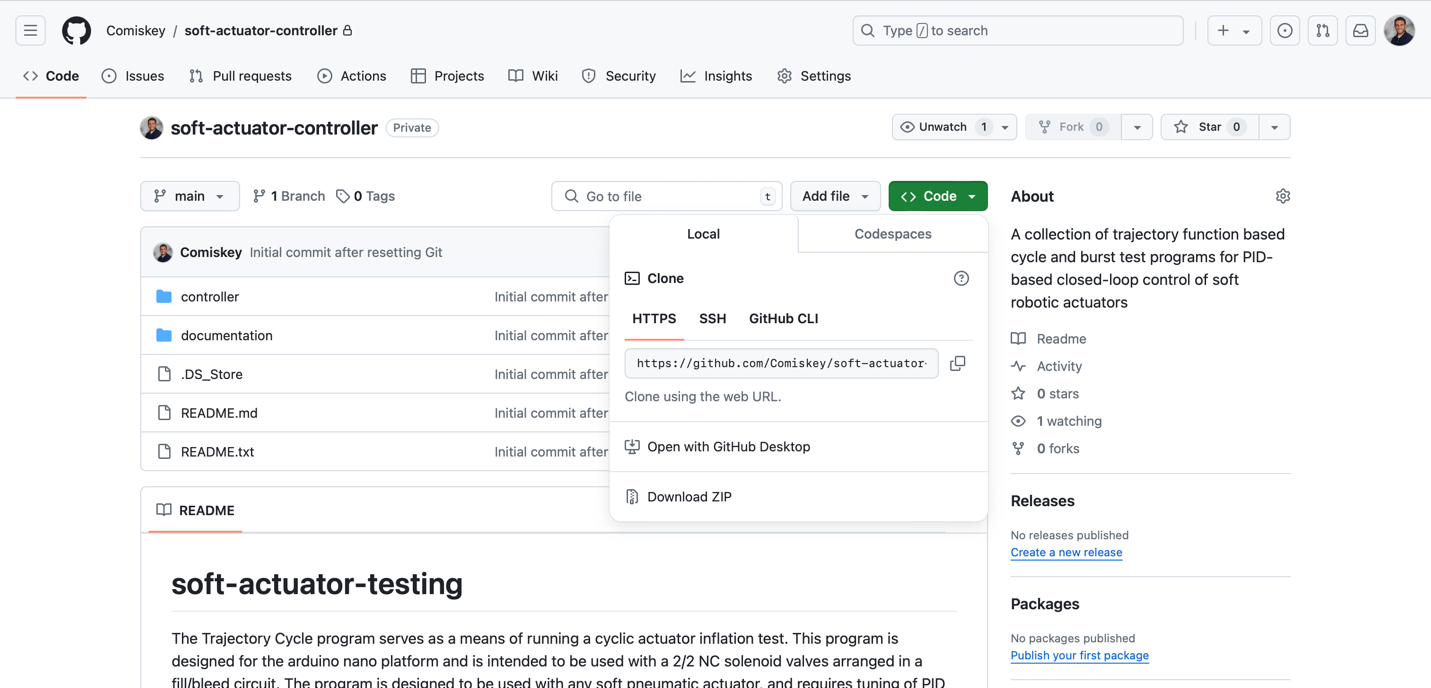
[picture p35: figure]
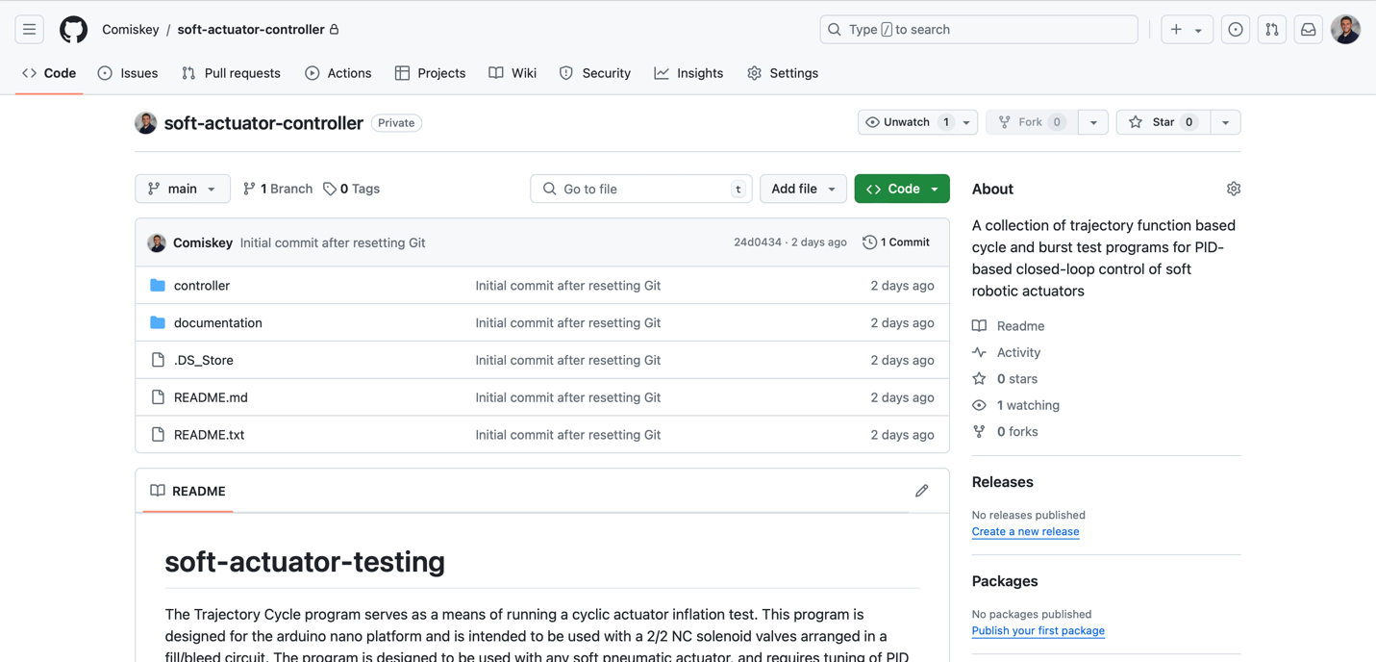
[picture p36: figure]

- Once here, click the green Code dropdown button, then click Download ZIP
- Unpack the contents of this zip file in an easily accessible file location.
  - Note that at this point, you should not interact with the code directly. The first time you open this folder in a code editor, you should do so through PlatformIO, following the steps explained below.

# 3. Setting up your Working Directory with PlatformIO

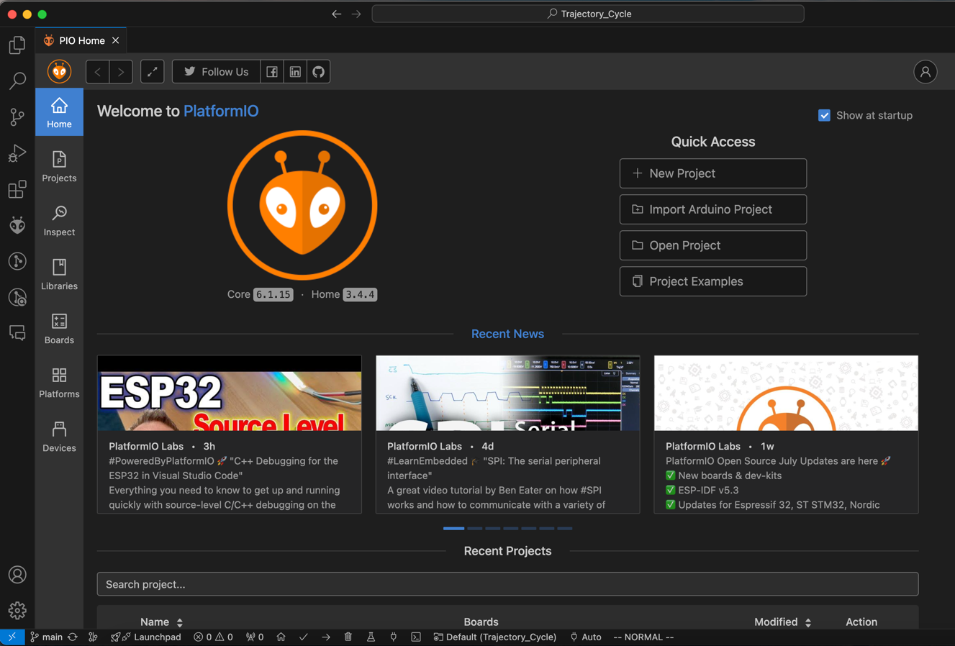
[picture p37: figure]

- Navigate to the PlatformIO home page and click the Import Arduino Project button
- An import menu will appear.
  - This menu has two parts: board selection and folder directory selection.
  - Click board selection, and type Nano into the search bar. From here,
    - select Arduino Nano ATmega328 (New Bootloader).

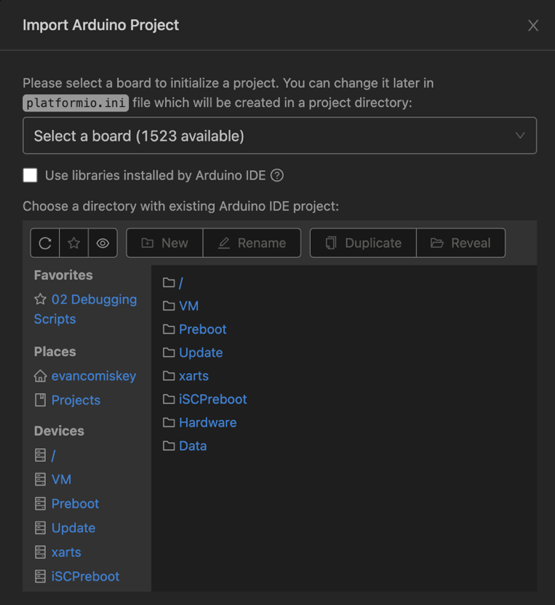
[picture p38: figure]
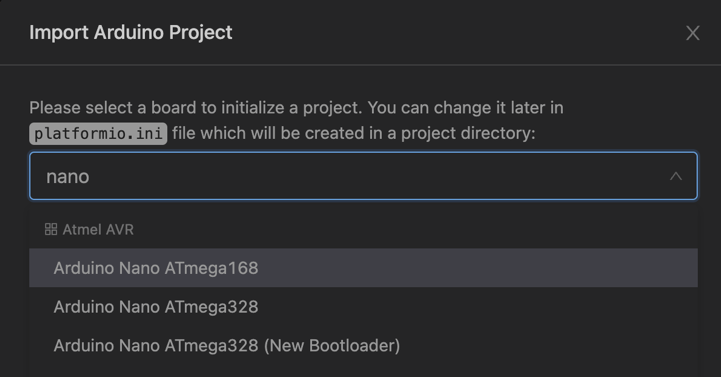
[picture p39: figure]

  - Click the Use Libraries installed by Arduino IDE checkbox to include necessary Arduino dependencies for the codebase.

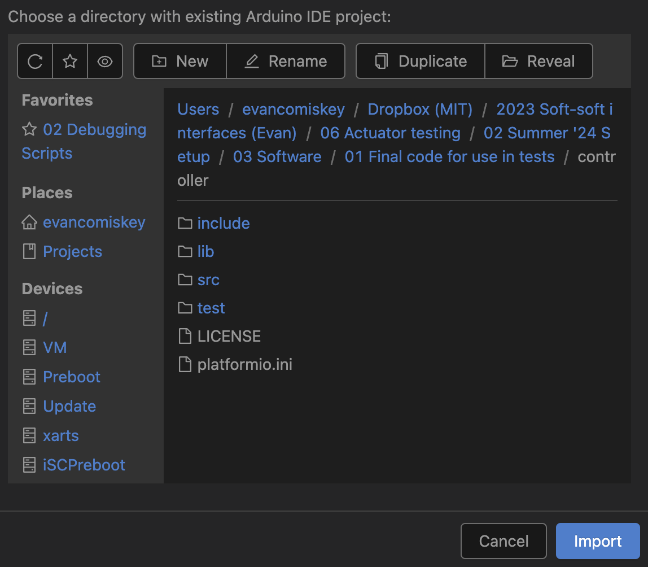
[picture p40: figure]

  - In folder directory selection, navigate to where you had previously unpacked the downloaded GitHub repository, then open the controller sub-folder. You should see the folder structure highlighted in blue in the directory selection sub-screen below. Once you do, click the Import button.
- You will have to redo this process if you decide to move the repository within your computer’s folder structure later, as PlatformIO will have to reinstall its dependencies in that new location.
- PlatformIO will begin automatically formatting the content of the directory to match the selected board once the project has been imported.
  - This may take a few minutes.
  - You can also change this later in the platform.ini file.
- Set-up will take a few seconds, but once completed, will bring you to the following screen:
- PlatformIO has opened the controller code’s directory in VS Code’s Explorer tab (highlighted in red above).
  - From now on, whenever you open the folder in VS Code, all necessary PlatformIO dependencies will open as well.
- You will know that PlatformIO is properly configured and running by the series of button options which will appear at the bottom of the screen when the directory is opened:
- Of these buttons, the most important are the following:
  - Home: Brings up the PlatformIO home page shown previously at the top of section 3
  - Build: Compiles all code in the directory. This button allows you to check the code for syntax errors without having to be directly connected to a microcontroller
  - Upload: Compiles, and sends the code to the microcontroller
  - Serial Monitor: Opens the serial monitor. Useful for set-up and general debugging
- Press the Build button to ensure that the directory has been properly configured as a PlatformIO project.

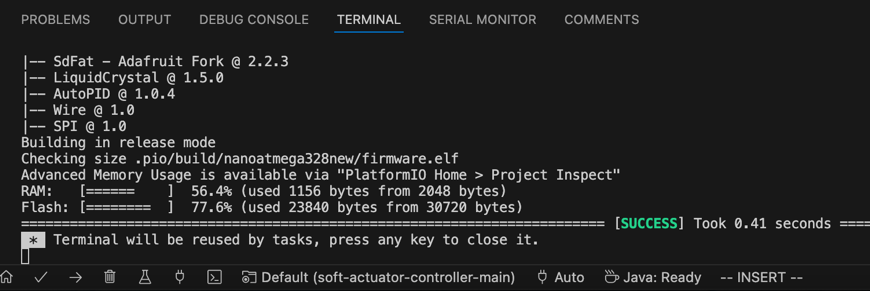
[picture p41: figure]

  - If it has been, the terminal will automatically open and present a success message after a few seconds as shown:
- Move on to running the controller once you see the success message appear in the terminal.


# 4. Running the Controller

- This section will cover how to run the controller during normal operation/cycle testing.
  - This section assumes that your solenoid valve has been properly tuned prior to your use of the stand. If this is not the case, please read through this section for context, before moving on to section 5 to walk through controller tuning procedures.
  - If someone in your group has successfully used the stand before, you do not need to read section 5.
- All settings relevant to the operation of the controller are found in a single file: adjustableSettings.cpp, which lives in the src folder.
  - adjustableSettings.cpp only contains variable definitions and is only relevant to quick set-up, adjustment, and use of the controller.
  - For a detailed explanation of what each variable does, please see the Test Stand & Controller Overview Word document.
- Ensure that the first 10 variables—pin definitions—match your electronics’ layout.
- Ensure that both TUNE_PRESSURE and TUNE_VENT are set to false.
  - Otherwise, the controller will operate in tuning mode, rather than as the normal controller.
- fileName is a string which sets the naming scheme for the tests you wish to run.
  - Files will automatically be generated on the system SD card in the form fileName_#.csv, where # represents the lowest unused integer value.
- USE_SD_CARD when true, will send all test data to the onboard SD card. The controller will not function properly without an SD card inserted in this state
  - When this Boolean is set to false, all data will be exported to the serial port, for use with MATLAB plotting scripts for faster gain-tuning workflows. All relevant data is still preserved in csv files automatically.
- The next relevant setting will be USE_KPA.
  - If true, it will record data in kilopascals.
  - If false, it will record in PSI.
  - Trajectory setpoints, as well as the overpressure limit, will automatically be interpreted in the units associated with this variable. Gains will be affected.
  - Whether USE_KPA is set to true or false is automatically included in the output file of a test.
- Next, select your delays for pressure reading/writing, interpolation, and controller action using PRESSURE_READ_DELAY, INTERP_CALC_DELAY, and CONTROLLER_DELAY respectively.
  - PRESSURE_READ_DELAY is the delay in milliseconds between each reading and logging of pressure data from the pressure sensor
    - The shorter the delay, the faster data files generated during tests will grow within a given time frame.
  - INTERP_CALC_DELAY is the delay in milliseconds between each interpolation between setpoints defined by the trajectory function
  - CONTROLLER_DELAY is the delay in milliseconds between controller actions, based on the most recent trajectory interpolations and pressure readings.
    - It is not recommended to set this value below the mechanical actuation time of your solenoid valve (25ms for the Clippard EFB-1DV-24-L used in the thesis discussing the controller)
- Then, set your PID gain values with KP, KI, and KD.
- Set the error THRESHOLD for the trajectory.
  - The smaller this value, the less error between the trajectory setpoint and the measured setpoint it will take to trigger the “failure to follow trajectory” test stop condition.
  - Units for THRESHOLD are automatically assigned based on the status of the USE_KPA Boolean.
- Once settings are adjusted to your liking:
  1. plug your computer into the USB port of the Arduino Nano on the electronics stand
  2. press the upload button highlighted in green in section 3, then wait for the terminal to display the success message
  3. unplug your computer from the microcontroller
  4. plug your electronics board into a 24V DC power supply
  5. connect your pressure source to the inlet pressure line.
  6. Plug your microSD card into the appropriate slot on the board.
  7. connect your volume line to your actuator, then open the line.
  8. turn the power to the board on.
- Once these steps are completed, the system will open the venting valve and close the inlet pressure to ensure the actuator is not unintentionally overinflated.
- Next, it will initialize the SD card.
  - During this initialization, a csv file is generated with the format of cycle_test_#.csv, where # is the first available lowest number not yet stored on the SD card. This file will contain all the data during that test.
    - If tests 1-9 and 11-12 are on the card, 10 will be written
  - If the Arduino is reset, or power to the board is turned off/lost at any point, the controller will consider this a new test, and begin writing to a new file upon start-up/reset.
  - Your specified settings remain stored on the microcontroller until the next upload, so you will only have to reupload code to the computer in the event you want to make new adjust any settings.
- Once the SD card has been initialized, the LCD on the electronics board will prompt you to press the start button to begin the test and will wait indefinitely for you to do so.
- After the start button is pressed, the test will begin.

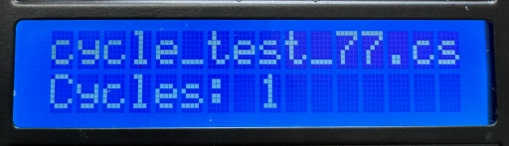
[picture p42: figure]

- During the test, the total number of completed cycles of your specified trajectory will be displayed on the LCD, along with the file on the SD card that data for this test is being written to. Example shown at right.
- Write down the name of this test file somewhere you will remember

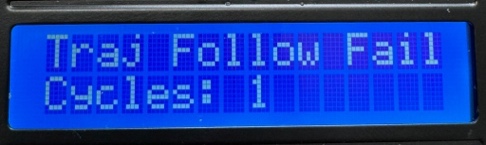
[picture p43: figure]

- When the test ends (stop pressed, failure to follow trajectory, or overpressure) the reason for test stoppage will replace the test file name on screen, as shown at right.
- Once a test has ended, power the board off with the switch.
- In all test-ending scenarios, the inlet valve is closed and then the venting valve is opened inside the solenoid.
  - The inside of the actuator volume is always reset to atmospheric pressure and is safe to remove from the pneumatic system.
- Disconnect/close your pressure source.
- Remove the SD card from its port to extract the data stored in the csv files onto your personal computer to process as you see fit.
  - So long as memory is available on the card, the controller program will never overwrite existing data on an SD card. Feel free to perform multiple tests before ever extracting data from the SD card.

# 5. Adjusting Settings & Tuning Your Solenoid

- This section will explain how to tune your controller to the specific solenoid valve used in your set-up.
- Even if you are using the same model of Clippard electronic valve listed in the BOM, you must still tune the controller to that specific 2/2 solenoid valve, as all solenoid valves physically vary to a slight degree.
  - If someone else in your group has used this system for tests before, you do not need to go through this tuning procedure, and just use the controller normally.
- To get started, set TUNE_PRESSURE to true as shown, and upload the code to the controller.
  - Ensure the end of your line to test is capped, such as with a closed valve.
- Power the system on before opening the inlet airline to the system
- Open the serial monitor on your computer by clicking the button specified in section 3.
  - The open serial monitor will look something like what is shown below.
- Set the Baud rate option to 115200. Connect to the appropriate port on your computer using the port dropdown menu.
  - If you are familiar with ArduinoIDE, the PlatformIO’s serial monitor behaves in the exact same way for projects build on the Arduino libraries.

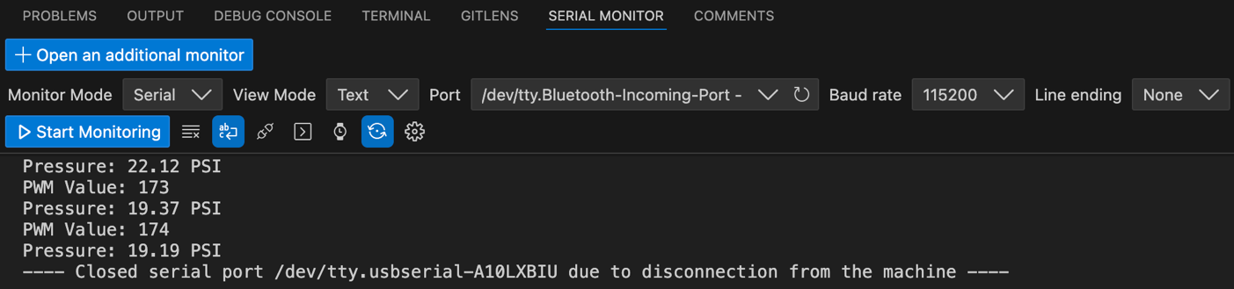
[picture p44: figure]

- Wait for the controller to go through its start-up routine; its steps displayed on the LCD on the electronics stand.

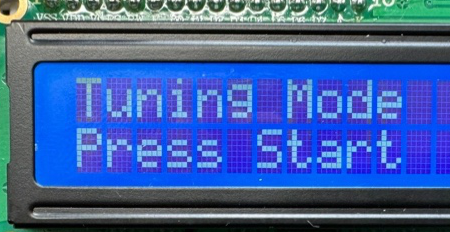
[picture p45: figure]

- Press the start button once prompted by the LCD display shown at left.
- You should now see pressure and PWM readings start to appear on the LCD.
  - If nothing is displaying, ensure you have pressed the start monitoring button, and are connect to the correct port on your personal device.
- With the pressure and PWM values being displayed at regular intervals in the serial monitor, now simply wait.
- At the point that the valve begins to open, you will see a change in the pressure reading on screen and hear a click or high-pitched whine coming from the solenoid.
- At this point, press the stop button on the electronics stand, but do not close or reset the serial monitor.
  - You will want to comb back through this pressure and PWM data to observe at what exact PWM value the valve began to open.
- Set ANALOG_PRESSURE_MIN to this value and save your change to the code.
- Repeat this entire process again, this time setting TUNE_PRESSURE false and TUNE_VENT to true.
  - As part of the vent valve tuning protocol, the volume line will fill for 0.1 seconds before holding both valves shut.
- You will then want to observe the serial monitor for decreases in pressure values as the PWM signal increases.
- Once you have determined which PWM value corresponds to the first noticeable decrease in pressure, set that value to ANALOG_VENT_MIN.
  - For a new Clippard EFB-1DV-24-L, expect the values to be in a nominal range between 120 and 200, and the mins and maxes to be roughly 30-40 values apart from one another.
- Now define the end of the corresponding ranges, also known as ANALOG_PRESSURE_MAX and ANALOG_VENT_MAX.
  - Based on prior testing, it is recommended to initially set both these values at their respective MIN value + 30 (i.e. 180, if your min value is 150).
- Once set, start tuning the controller gains to your specific actuator of choice using the normal operating procedures detailed in section 4.
  - If during this PID gain tuning, you find that the controller produces bang-bang control-like hysteresis around your setpoints, consider reducing the PWM range that can be written to the solenoids by reducing the values of either MAX variable as appropriate.
    - bang-bang-like behavior during periods of positively sloping trajectory should be met with decreases to ANALOG_PRESSURE_MAX, and bang-bang-like behavior during periods of negatively sloping trajectory should be met with decreases to ANALOG_VENT_MAX.
  - If you instead find that the controller is incapable of producing responses within what you consider a reasonable timeframe, consider increasing the PWM range that can be written to the solenoids by increasing the MAX values when appropriate following the same positive/negative slope checks as above.

# 6. Processing Test Data

- This section explains how to get started processing your test data, using the included MATLAB processing scripts as a jumping off point for your own analysis.

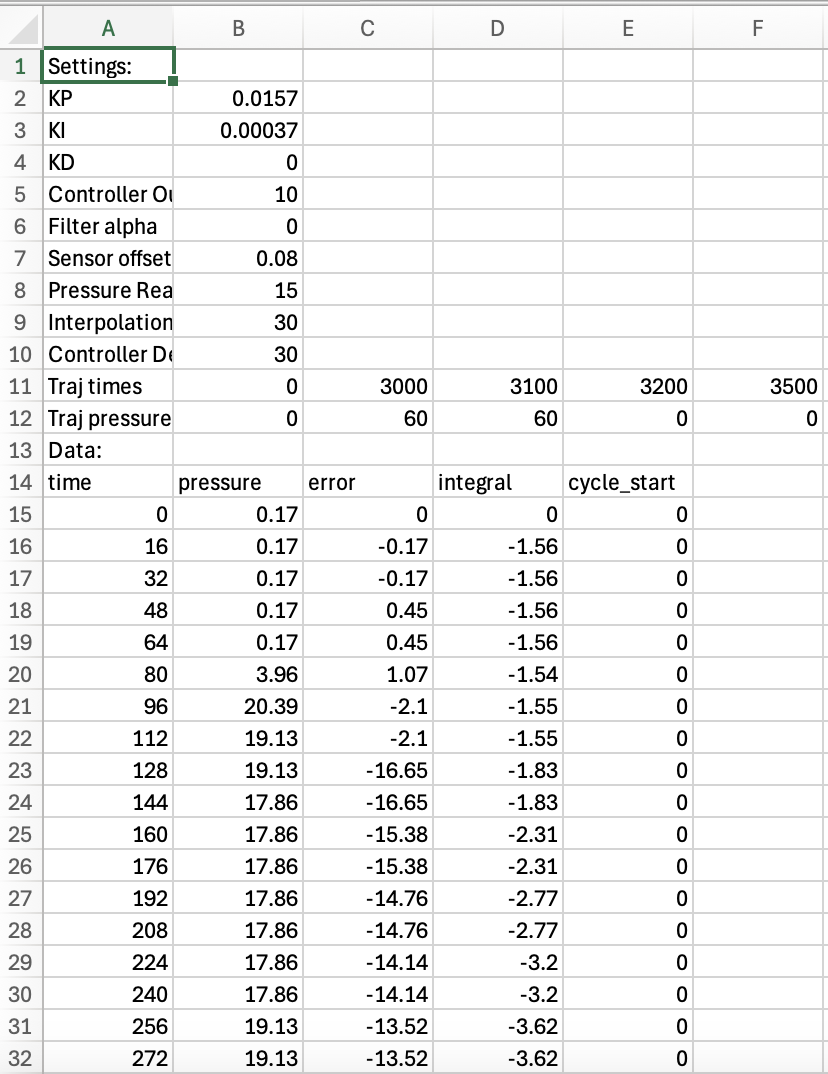
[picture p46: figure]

- A test file from this controller automatically includes the relevant settings used in the associated test, as well time data in milliseconds, pressure, the controller error and integral values, and a cycle start marker. This is organized as shown:
- Included in the repository for this controller are several MATLAB scripts: DebuggingDashboard.m, SerialPlotting.m, and PressureVsTimeOverlap.m, along with a few helper functions.

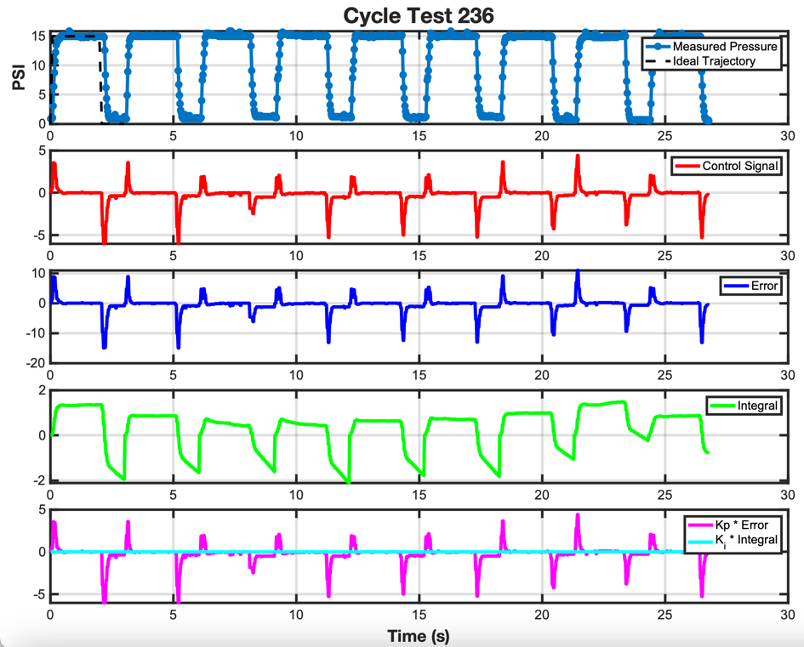
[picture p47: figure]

- DebuggingDashboard.m displays the behavoir of the controller over time based on the specific Kp and Ki values used for a given test test to help determine optimal controller behavoir. It produces plots like shown:
- SerialPlotting.m generates a similar graph in real time, using the same data used to generate the test files, transferred via serial to a computer. All relevant data is automatically saved to a csv file with the naming scheme fileName_MATLAB_#.csv

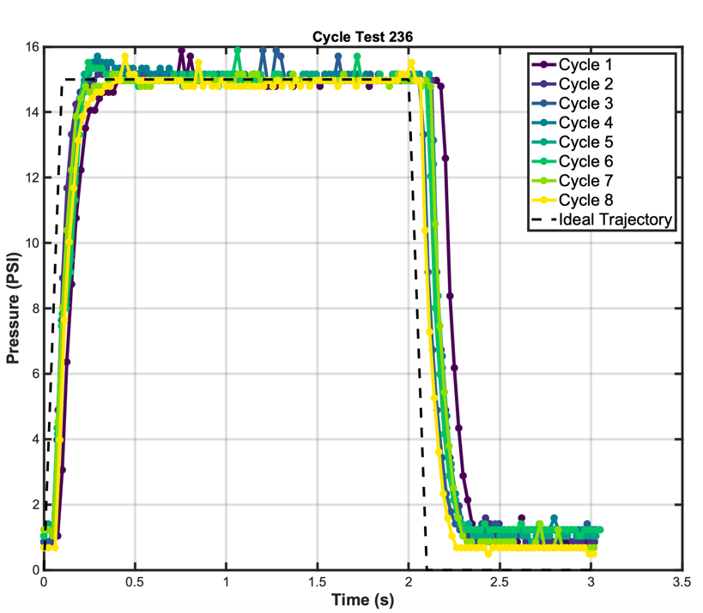
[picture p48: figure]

- PressureVsTimeOverlap.m displays all completed cycles from the test overlayed atop one another, using the cycle_start (normally 0) variable to deliniate the start and end (demarked as 1) of each cycle.
  - This script is helpful for quick data sharing, and for checking cycle-to-cycle consistency of the controller with your acutator
- Both helper funtions additionally plot an Ideal Trajectory reference function, which is plotted by defining the trajectory function in the getTracjectory.m helper function in the helper functions folder, in the same way as defined in the controller
  - See Write Custom Trajectory Functions for more information

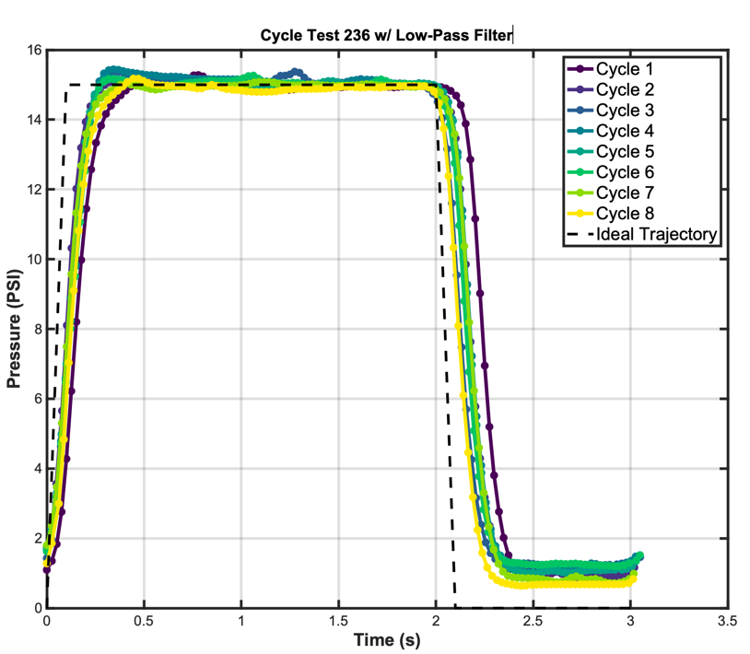
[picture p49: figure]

- Additionally, there is a digital low-pass filter functionality included to allow for curve smoothing for creation of prettier graphs
  - This feature is set to off/false by default

# Controller architecture and operating principles

- High-level: PID controller with anti-windup and clipping of control signal
  - Measured and desired signal: pressure
  - Commanded signal: duty cycle of two solenoid valves
  - Controller will loop the programmed pressure trajectory infinitely until test fails or is manually stopped
  - To avoid windup, controller resets between repeated cycles of the trajectory
- Startup protocol
- End-of-test logic: a test should automatically end when any of the following conditions are met
  - Overpressure triggered
    - If sensor reads above OVERPRESSURE_LIMIT, vent and end test
    - Reason for test end: “Overpressure”
  - Controller cannot follow programmed trajectory
    - if (traj.failingToFollow(SensorPressure, deltaT, THRESHOLD)) {}
- Data logging

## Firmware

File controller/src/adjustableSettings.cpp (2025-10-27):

#include <Arduino.h>
#include "adjustableSettings.h"

// ========== Pin Definitions ==========
/* Pins pins used to connect various components to the microcontroller.
   Adjust to your specific hardware set-up. Ensure PRESSURE_PIN and VENT_PIN are connected
   to PWM-capable pinouts on your microcontroller*/

const int START_BUTTON_PIN = A3; 
const int STOP_BUTTON_PIN = A2;
const int SENSOR_PIN = A7;
const int PRESSURE_PIN = 6;
const int VENT_PIN = 5;

// ORIGINAL PINOUTS
// const int START_BUTTON_PIN = A3; 
// const int STOP_BUTTON_PIN = A2;
// const int SENSOR_PIN = A7;
// const int PRESSURE_PIN = 6;
// const int VENT_PIN = 5;



// ========== Pneumatic Valve Settings ==========
/* Control the pressure applied by the pneumatic valves.
   Adjust the min and max analog PWM write values to calibrate the pressure range. */
const int ANALOG_PRESSURE_MIN = 157;
const int ANALOG_PRESSURE_MAX = 182;
const int ANALOG_VENT_MIN = 164;
const int ANALOG_VENT_MAX = 189;

// ========== Filename Settings ==========
/* String for name of file series. Controller will automatically generate csv
   file with lowest available integer appended to the end, so as to not overwrite 
   existing data files on the SD card */

const char fileName[] = "251023_cycle";

// ========== Tuning Modes ==========
/* Toggles for the initial tuning processes for the pressure and vent solenoid valves,
   and the default operation of the controller. Set 'TUNE_PRESSURE' to 'true' to enable tuning mode 
   for the pressure valve, and 'TUNE_VENT' to 'true' to enable tuning mode for the vent valve. 
   Set both to 'false' for normal PID controller operation. */

const bool TUNE_PRESSURE = false;
const bool TUNE_VENT = false;

// ========== Pressure Sensor Settings ==========
/* Settings related to pressure sensor calibration and data logging.
   Adjust the filter alpha value and maximum pressure according to your sensor's specifications.
   Toggle where you want to use kPa (true) or PSI (false) depending on your application/preference */

const bool USE_SD_CARD = true;
const bool USE_KPA = false; 
const double FILTER_ALPHA = 0.0;
const int OVERPRESSURE_LIMIT = 17.4; // units depend on value of USE_KPA
const double SENSOR_OFFSET = 0.11; // Offset used to calibrate a specific sensor

// ========== Frequency Settings ==========
/* Specifiy delay between different tasks are executed. Adjusting these 
values lets you control the time delay, in milliseconds, between each occurrence 
of the corresponding action in the system. */

const double PRESSURE_READ_DELAY = 30; // milliseconds
const int INTERP_CALC_DELAY = 30;      // milliseconds
const int CONTROLLER_DELAY = 30;       // milliseconds 

// ========== PID Controller Settings ==========
/* These settings configure the PID controller that regulates pressure.
   Fine-tune the proportional (KP), integral (KI), and derivative (KD) 
   constants for optimal performance. */

const double THRESHOLD = 4.35;
const int OUTPUT_MIN = -1.0; // DO NOT CHANGE
const int OUTPUT_MAX = 1.0; // DO NOT CHANGE
const double KP = 0.72;	  // Start with Kp = 0.1, Ki = 0.0, Kd = 0.0 for Zeigler-Nichols tuning
const double KI = 3.38;
const double KD = 0.0;

// ========== Trajectory Settings ==========
/* Definition for the pressure trajectory over time.
   Choose one trajectory type and ensure the first and last pressures match for smooth cycling.
   Ensure that the size of the TIMES and PRESSURES arrays match.
   
   Example Trajectories:
   - Step function
   - Triangle
   - Sawtooth
   - Reverse Sawtooth
   - Sinusoidal
   - Burst Ramp
   - Linear Ramp
*/

// Step Function Trajectory
const float TIMES[] = {0, 100, 1500, 1600, 3000}; // milliseconds
const double PRESSURES[] = {0, 8.7, 8.7, 0, 0};   // PSI or Kpa


// const float TIMES[] = {0, 100, 2000, 2100, 4000}; // milliseconds
// const double PRESSURES[] = {0, 5.8, 5.8, 0, 0};    // PSI or Kpa

// Uncomment to use a different trajectory:

// Triangle Trajectory
// const float TIMES[] = {0, 2000, 4000}; // milliseconds
// const double PRESSURES[] = {0, 7.2, 0}; // PSI or Kpa
// const float TIMES[] = {0, 1000, 2000, 3000, 4000}; // milliseconds
// const double PRESSURES[] = {0, 5.8, 5.8, 0, 0}; // PSI or Kpa

//Sawtooth Trajectory
// const float TIMES[] = {0, 3000, 3100, 3200, 3500}; // milliseconds
// const double PRESSURES[] = {0, 5.8, 5.8, 0, 0};    // PSI or Kpa

// Reverse Sawtooth Trajectory
// const float TIMES[] = {0, 100, 200, 3100, 3500}; // milliseconds
// const double PRESSURES[] = {0, 20, 20, 0, 0};   // PSI or Kpa

// Sinusoidal Trajectory
// const int amp = 20; // adjust amplitude of sinusoidal wave
// const float TIMES[] = {0, 1111, 2222, 3333, 4444, 5555, 6666, 7777, 8888, 10000, 10500}; // milliseconds
// const double PRESSURES[] = {
//     0, 
//     amp * sin(M_PI / 9 * 1), 
//     amp * sin(M_PI / 9 * 2), 
//     amp * sin(M_PI / 9 * 3), 
//     amp * sin(M_PI / 9 * 4), 
//     amp * sin(M_PI / 9 * 5), 
//     amp * sin(M_PI / 9 * 6), 
//     amp * sin(M_PI / 9 * 7), 
//     amp * sin(M_PI / 9 * 8), 
//     0,
//     0
// }; // PSI or Kpa

// Burst Ramp Trajectory
// const float TIMES[] = {0, 5000, 10000, 15000, 20000, 
//                         25000, 30000, 35000, 40000, 45000, 
//                         50000, 55000, 60000, 65000, 70000, 
//                         75000, 80000, 80100, 80500}; // milliseconds
// const double PRESSURES[] = {0, 5, 5, 10, 10, 
//                             15, 15, 20, 20, 25, 
//                             25, 30, 30, 35, 35, 
//                             40, 40, 0, 0}; // PSI or Kpa

// Linear Ramp Trajectory
// const float TIMES[] = {0, 180000, 180100}; // milliseconds
// const double PRESSURES[] = {0, 20, 0};     // PSI or Kpa


// ========== Unadjustable Variables ==========
/* DO NOT CHANGE
   These variables are based upon the adjustable settings above, and are
   set automatically so as to make the front-end user expierence simpler */
const int TRAJ_SIZE = sizeof(TIMES) / sizeof(TIMES[0]);

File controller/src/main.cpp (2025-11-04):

// Library Inclusions
#include <Arduino.h>
#include <Wire.h>
#include <AutoPID.h>

// Custom Inclusions
#include "sdCardOperations.h"
#include "analogPressureSensor.h"
#include "valveControl.h"
#include "lcdDisplay.h"
#include "trajectory.h"
#include "valveTuning.h"
#include "adjustableSettings.h"

// Declare dynamic variables
float lastPressureUpdate; // milliseconds
float lastInterpUpdate; // milliseconds
float cycleStartTime; // milliseconds
float trajStartTime; // milliseconds
int totalCycles = 0; 
unsigned long deltaT;
bool cycleComplete = false;
double desiredPressure; // PSI
double output;

// Initialize controller and trajectory objects
AutoPID valvePID(&SensorPressure, &desiredPressure, &output, OUTPUT_MIN, OUTPUT_MAX, KP, KI, KD);
Trajectory traj(TRAJ_SIZE);

// helper function to display test end condition, # of cycles and exit
void endTest(String reason, int cycles){
  closePressureValve();
  vent();
  valvePID.stop();
  if(USE_SD_CARD){
    closeSD();
  }
  setLCD(reason, "Cycles: " + String(totalCycles));
  exit(0);
}

void setup() {
  // Initialize Serial w/ Baud Rate 115200
  Serial.begin(115200);
  // Initialize LCD
  lcd.init();
  lcd.backlight();
  // Initialize valves and pressure sensor
  pinMode(PRESSURE_PIN, OUTPUT);
  pinMode(VENT_PIN, OUTPUT);
  pinMode(SENSOR_PIN, INPUT);
  analogReference(DEFAULT);
  pinMode(START_BUTTON_PIN, INPUT_PULLUP);
  pinMode(STOP_BUTTON_PIN, INPUT_PULLUP);

  // vent any air in the system
openVentValve();
delay(1000);

closeValves();
delay(20); // 20 millisecond delay between signal and mechanical valve response

  // openVentValve();

  // openPressureValve();
  // delay(1000);
  // closeValves();
  // delay(1000);

  // openVentValve();
  // delay(1000);
  // closeValves();


  // // TODO TROUBLESHOOT VENTING
  setLCD("Initializing...", "");
  Serial.println("Initializing...");
  // Serial.println(digitalRead(START_BUTTON_PIN));
  // Serial.println(digitalRead(STOP_BUTTON_PIN));
  // closePressureValve();
  // setLCD(F("Venting..."), F("Please wait"));
  // Serial.println("NEW RUN");

  // Serial.println("Venting");
  // Serial.println(analogRead(SENSOR_PIN));
  // openVentValve();
  // delay(5000); // hold for 5 seconds to fully vent
  // Serial.println(analogRead(SENSOR_PIN));
  // closeValves();  


  // delay(5000);

  // // // TODO TROUBLESHOOT PRESSURIZING
  // closeVentValve();
  // setLCD(F("Pressurizing..."), F("Please wait"));
  // Serial.println("Pressurizing");
  // Serial.println(analogRead(SENSOR_PIN));
  // openPressureValve();
  // delay(5000); // hold for 5 seconds to fully pressurize
  // Serial.println(analogRead(SENSOR_PIN));

  // closePressureValve();
  // openVentValve();
  // delay(1000);
  // closeValves();
  // delay(50);

  // closePressureValve();
  // Serial.println("Venting");
  // Serial.println(analogRead(SENSOR_PIN));
  // openVentValve();
  // delay(5000); // hold for 5 seconds to fully vent
  // Serial.println(analogRead(SENSOR_PIN));
  // closeValves();  

  // Serial.println("Venting");
  // closePressureValve();
  // openVentValve();
  // delay(5000);
  // Serial.println(analogRead(SENSOR_PIN));
  // closeValves(); 
  // Serial.println(analogRead(SENSOR_PIN));


  if(TUNE_PRESSURE || TUNE_VENT){ // Solenoind Valve Tuning Mode    
    // Ensure only one valve is set for tuning
    if (TUNE_PRESSURE && TUNE_VENT) {
      setLCD(F("Error"), F("Only 1 Valve"));
      exit(0);
    }
    setLCD(F("Tuning Mode"), F("Press Start"));
    while(digitalRead(START_BUTTON_PIN) == HIGH){
      // wait for start button press
    }
    delay(2000);
    // begin tuning process
    setLCD(F("Starting Tuning..."), F("Please wait"));
  }
  // otherwise, normal operation
  else{ 
  // Initialize SD Card if using it
    if (USE_SD_CARD) {
      if (!initializeSDCard()) {
        while (1);
      }
      delay(100);
    }
    else{
      Serial.println(F("Settings:"));
      Serial.print(F("filename,")); Serial.println(fileName);
      Serial.print(F("Use KPA?,")); Serial.println(USE_KPA);
      Serial.print(F("KP,")); Serial.println(KP, 5);
      Serial.print(F("KI,")); Serial.println(KI, 5);
      Serial.print(F("KD,")); Serial.println(KD, 5);
      Serial.print(F("Traj Follow Error Threshold,")); Serial.println(THRESHOLD);
      Serial.print(F("Filter alpha,")); Serial.println(FILTER_ALPHA, 5);
      Serial.print(F("Sensor offset,")); Serial.println(SENSOR_OFFSET, 5); 
      Serial.print(F("Pressure Read Delay,")); Serial.println(PRESSURE_READ_DELAY);
      Serial.print(F("Interpolation Calculation Delay,")); Serial.println(INTERP_CALC_DELAY);
      Serial.print(F("Controller Delay,")); Serial.println(CONTROLLER_DELAY);
      Serial.print(F("Traj times,"));
      for (int i = 0; i < TRAJ_SIZE; i++) Serial.print(TIMES[i]), Serial.print(i < TRAJ_SIZE - 1 ? ',' : '\n');
      Serial.print(F("Traj pressures,"));
      for (int i = 0; i < TRAJ_SIZE; i++) Serial.print(PRESSURES[i]), Serial.print(i < TRAJ_SIZE - 1 ? ',' : '\n');
      Serial.println(F("Data:"));
      Serial.println(F("UPDATED TEXT"));
    }
    // Initialize trajectory
    if(!InitializeTrajectory(&traj, TIMES, PRESSURES, TRAJ_SIZE)){
      setLCD(F("Traj Error"), F("Check Serial"));
      while(1);
    }

    // Set PID Controller settings
    valvePID.setTimeStep(CONTROLLER_DELAY); //milliseconds.
    // Tells AutoPID to NOT use bang-bang control
    valvePID.setBangBang(0, 0);

    // hold until start button pressed.
    setLCD(F("Press Start"), F("to Begin Test"));
    while(digitalRead(START_BUTTON_PIN) == HIGH){
      // wait for start button press
    }
    delay(2000);
    // begin cycle test
    setLCD(String(specificFileName), "Cycles: " + String(totalCycles));
    testStartTime = millis();
    trajStartTime = millis();
    traj.reset();
  }
}

void loop() {
  // Get current time
  // Serial.println("START LOOP");
  unsigned long currentMillis = millis();
  // Stop operations if stop button is pressed
  if (digitalRead(STOP_BUTTON_PIN) == LOW){
    endTest(F("Stop Pressed"), totalCycles);
  }

  // TODO REMOVE THIS
  // Print current reading on sensor pin
  // Serial.println(analogRead(SENSOR_PIN));
  // Serial.println((5.0 * analogRead(SENSOR_PIN) / 1023.0 - 0.5) * 37.5);

  // Pressure valve tuning-=
  if (TUNE_PRESSURE) { 
    Serial.println("TUNING PRESSURE VALVE");
    
    tuneValve(PRESSURE_PIN);
    setLCD(F("Pressure Valve"), F("Tuning Complete"));
    exit(0);
  }
  // Vent valve tuning
  else if (TUNE_VENT) { 
    tuneValve(VENT_PIN);
    setLCD(F("Pressure Valve"), F("Tuning Complete"));
    exit(0);
  }
  // Normal operation
  else { 


    // Check that pressure does not exceed maximum
    if (SensorPressure > OVERPRESSURE_LIMIT) {
      vent();
      endTest(F("Overpressure"), totalCycles);
    }



    // Check that controller isn't failing to follow the trajectory
    if (traj.failingToFollow(SensorPressure, deltaT, THRESHOLD)) {
      endTest(F("Traj Follow Fail"), totalCycles);
    }



    // Check if cycle is complete
    if (cycleComplete) {
      
      // Update cycle count and LCD
      totalCycles++;
      setLCD(String(specificFileName), "Cycles: " + String(totalCycles));

      // Reset controller (anti-windup) and trajectory
      valvePID.reset();
      traj.reset();

      // Log and sync data
      logData(SensorPressure,
              valvePID.getPreviousError(),
              valvePID.getIntegral(),
              cycleComplete,
              currentMillis);
      trajStartTime = millis();
      syncData();

      // Update cycle status
      cycleComplete = false;
    }



    // Log data at (1/PRESSURE_READ_DELAY) Hz
    if ((currentMillis - lastPressureUpdate) > PRESSURE_READ_DELAY) {

      // Measure pressure
      UpdateFilteredSensorPressure(USE_KPA);

      // Log data
      logData(SensorPressure,
              valvePID.getPreviousError(),
              valvePID.getIntegral(),
              cycleComplete,
              currentMillis);

      // Reset time since last pressure update
      lastPressureUpdate = currentMillis;
    }

  

    // Interpolate setpoint at (1/INTERP_CALC_DELAY) Hz
    if ((currentMillis - lastInterpUpdate) > INTERP_CALC_DELAY) {

      // Calculate time since start of trajectory cycle
      deltaT = currentMillis - trajStartTime; // COULD FUCK UP THE ENTIRE PROGRAM

      // If trajectory is finished, update current pressure and cycle status
      if (traj.isFinished(deltaT)) {
        desiredPressure = PRESSURES[TRAJ_SIZE - 1];
        cycleComplete = true;
      }
      
      // If trajectory isn't finished, interpolate current setpoint
      else {
        desiredPressure = traj.interp(deltaT);
      }

      // Reset time since last setpoint interpolation update
      lastInterpUpdate = currentMillis;
    }


    // Run the PID control action
    valvePID.run();
    sendSignalToValves(output);
  }
}

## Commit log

2024-09-27 Optimize SD card write operations to decrease loop cycle time. Added pressure sensor offset variable. Increased SD clock speed to 8 Mhz.
2024-09-30 Optimized trajectory class and use of millis() calls
2024-12-13 Final commit for thesis submission. Updated to be accurate to all statements made in both documentation and thesis. Switched LCD libraries to work with 4-pin carrier board. Lowered maximum trajectory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
2025-10-03 Add design documents
    - CAD, kicad, BOM
    [2020 rail - M5 corner bracket.SLDPRT, 91290A140_Alloy Steel Socket Head Screw.SLDPRT, ActuatorMount - 1-8NPT.SLDPRT, ActuatorPlate.SLDPRT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]
2025-10-03 Update CAD references
    [2020 rail - M5 corner bracket.SLDPRT, 91290A140_Alloy Steel Socket Head Screw.SLDPRT, ActuatorMount - 1-8NPT.SLDPRT, ActuatorPlate.SLDPRT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]
2025-10-07 Add CAD for electronics box
    [Electronics box (Entity_0).DXF, Electronics box (Entity_1).DXF, Electronics box.SLDPRT]
2025-10-07 Minor edits to data processing scripts
    - Update reference from "helper functions" to "helper_functions"
    - Add trial data and data directory
    [251007_setup_0.csv, 251007_setup_1.csv]
2025-10-07 Tune PID for Cat's fPNs
    [251007_setup_MATLAB_1.csv, 251007_setup_MATLAB_10.csv, 251007_setup_MATLAB_11.csv, 251007_setup_MATLAB_12.csv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]
2025-10-07 Update test frame actuator mounting
    [2020 rail - M5 corner bracket.SLDPRT, 91290A140_Alloy Steel Socket Head Screw.SLDPRT, Actuator - Cat baseline.SLDPRT, Actuator - Cat baseline.STEP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]
2025-10-24 Small updates to valve tuning
    - Print information about tuning to Serial monitor during tuning process
2025-10-24 Add valve and PID tuning data
    [251007_setup_MATLAB_26.csv, 251007_setup_MATLAB_27.csv, 251007_setup_MATLAB_28.csv, 251007_setup_MATLAB_29.csv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]
2025-10-27 Update controller properties and migrate data
    [250828_setup_0.csv, 250828_setup_1.csv, 250828_setup_2.csv, 251007_setup_0.csv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]
2025-11-04 Add raw .csv data from cycle testing
    [250828_setup_0.csv, 250828_setup_1.csv, 250828_setup_2.csv, 251007_setup_0.csv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]
2025-11-04 Add processed files/figures and update specimen tracking sheet
    - Add cycle_combined_specimen00.mat to .gitignore based on large size (>100 MB)
    [file tracking.xlsx]
2025-11-05 Debug controller end-of-test conditions
    [file tracking.xlsx]
